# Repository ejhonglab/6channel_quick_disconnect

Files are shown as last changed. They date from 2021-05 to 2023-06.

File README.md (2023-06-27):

This assembly aims to allow rapidly exchanging groups of 6 odor vials.

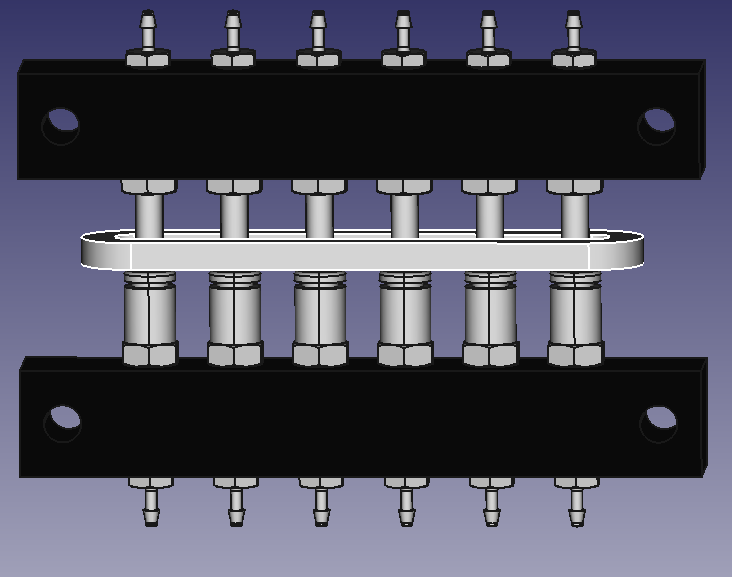
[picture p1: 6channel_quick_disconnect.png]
CAD model


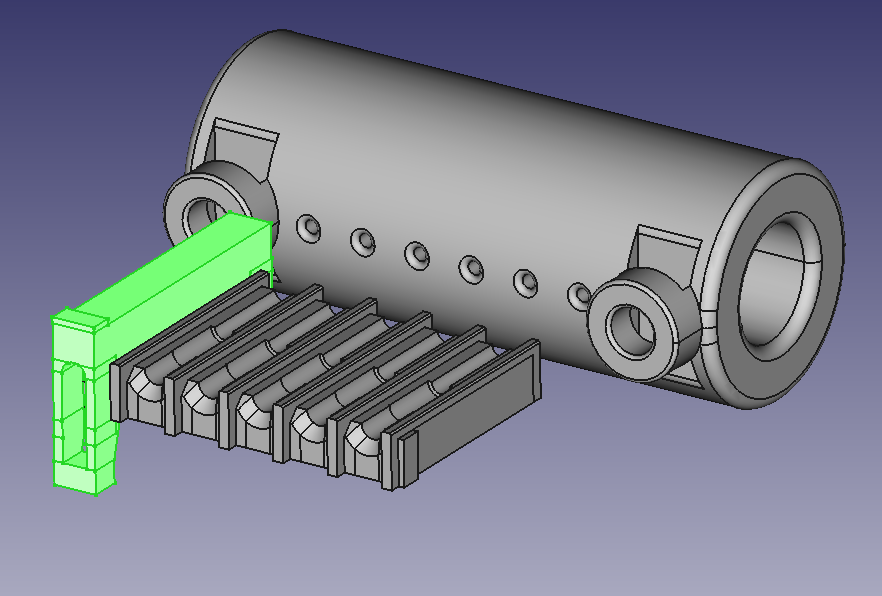
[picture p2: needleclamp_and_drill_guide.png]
Needleclamp and drill guide


### Bill of materials

| Description | McMaster Part Number | Quantity |
| ---         | ---                  | ---      |
| 5/32" OD tube stem to 10-32 thread | [5779K623](https://www.mcmaster.com/5779K623) | 6 |
| Junction block (6 position, 10-32 thread) | [5091K61](https://www.mcmaster.com/5091K61) | 1 + 1 per-exchangeable-side |
| Female 5/32" OD push-to-connect to 10-32 thread | [7880T115](https://www.mcmaster.com/7880T115) | 6 per-exchangeable-side |
| 10-32 thread to barb for 1/16" ID tube | [2974K123](https://www.mcmaster.com/2974K123) | 6 + 6 per-exchangeable-side (2 packs of 10) | 
| Release bar | N/A (3D printed from `release_bar.stl`) | 1 |
| Mounting screws | [92185A992](https://www.mcmaster.com/92185A992) | 1 (25 pack) |

The [tube stems (5779K623)](https://www.mcmaster.com/5779K623) can each be replaced with
a combination of an additional [female push-to-connect (7880T115)](https://www.mcmaster.com/7880T115)
and a [female-to-female tube stem adapter (5779K349)](https://www.mcmaster.com/5779K349)
, which is substantially cheaper at current prices. Making this substitution will
introduce another joint that could be more likely to leak.

See our [11-channel olfactometer repo](https://github.com/ejhonglab/11channel_olfactometer)
for the context in which we use this assembly, along with a parts list to build it.

### Assembly

To drill the 6 holes the needles will be inserted into (in the 1/4" ID, 3/8" OD PTFE
tube; see 11 channel olfactometer bill of materials), print
`needle_drill_guide_for_ptfe_tube.stl` and lightly clamp it do the PTFE tube using M3
fasteners. `needle_drill_guide_for_ptfe_tube.3mf` should contain the same model as the
STL, but also has a support enforcer to only generate supports in a place where they
should be easy to remove. Use a smaller drill than the diameter of the needles (maybe <=
3/64"), and you should be able to get several uses out of the drill guide. If making
several rows of holes, offset them enough so that the needles will not interfere with
each other when inserted.

`needleclamp_top_with_supports.stl` should be printed in an orientation where one side
of each latch is flat against the bed, so that layer lines do not make the latch more
fragile.  I used PETG and a 0.4mm nozzle, without many changes to the bridging settings,
and no supports added. Any internal supports would make the part harder to clean up, and
doing so would risk damaging the latches, so the part has a rectangle opposite the space
for the needle, which you should cut off of each latch (e.g. with a razor blade). An
initial attempt to print the part using a 0.6mm nozzle did not make good parts, because
the bridging performance was different, although limited internal supports or different
settings could possibly fix that. I leave one of these parts semi-permanently attached
to the end of each odor vial I'm actively using, to minimize setup time.

### 3D-printed parts

All parts (except the drill guide) should be printed with high infill. I used 100%.

I printed most parts on a Prusa i3 MK3S with PETG filament. All parts should be
printable with either a 0.4 or 0.6mm nozzle, *except* `needleclamp_top.stl`, which I so
far only got good parts with a 0.4mm nozzle.

I used PrusaSlicer
`2.2`-`2.3` to slice the `.stl` files to `.gcode`.

#### Regenerating STLs

To generate `release_bar.stl`:
1. Open `6channel_quick_disconnect.FCStd` in FreeCAD
2. Select `release_bar` in the tree view at the left. May need to expand
   `6channel_quick_disconnect` first.
3. `File->Export` (or `Ctrl-e`). Under the `Files of type:` menu at the bottom, select
   `STL Mesh (*.stl *.ast)`. Rename file to `release_bar.stl`. Press `Save`.

`needle_clamp_and_drill_guide.FCStd` contains the models for:
- `needleclamp_top_with_supports.stl`
- `needleclamp_bottom.stl`
- `needle_drill_guide_for_ptfe_tube.stl`

The `*.FCStd` files were produced with FreeCAD `0.19`-`0.20`.

The models for the McMaster-Carr parts in `6channel_quick_disconnect.FCStd` came from
the McMaster website.

### Operation

#### Push-to-connect (air inputs to odor vials)

Before matching the two sides of this assembly (i.e. pushing the tube stems into the
female push-to-connect adapters), check that you have a release bar placed around the
row of male tube stems. Then, firmly squeeze both sides of the assembly from the
aluminum passthru blocks. To disconnect the two sides of the assembly, press the release
bar down (so it presses all of the release rings on the female push-to-connect
fittings), and then pull the two sides apart.

#### Needleclamp (odor vial outputs)

Both the top and bottom of the needleclamp have a ridge to indicate which side has a
wider internal diameter. The clamp tops should be inserted so that their ridge is on the
same side as the ridge on the clamp bottom, and the section of the needle covered with
the PTFE tubing should go in this half of the clamp.

The section of the needle with PTFE tube over it should go (at most) halfway down the
needleclamp top, as if the PTFE overlaps with the thinner internal diameter of the
needleclamp top, the top and bottom of the clamp won't close all the way. When all slots
in the clamp are populated, the top surfaces of all the clamp tops should be flat. If
any are sticking out, check whether the PTFE section is inserted too far. If the needles
are not in a straight enough line to insert, it also likely indicates a clamp is not
seated fully.

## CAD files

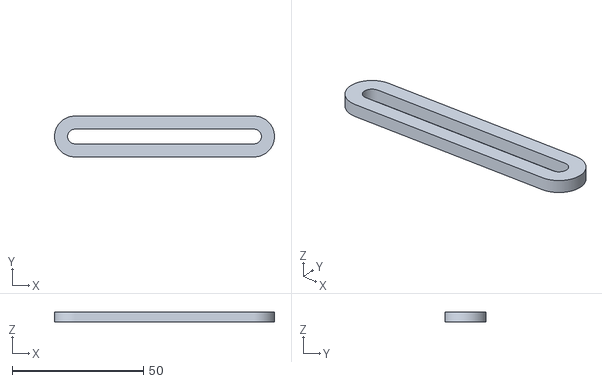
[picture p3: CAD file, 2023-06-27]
release_bar.stl
83.9 x 15.6 x 4.00

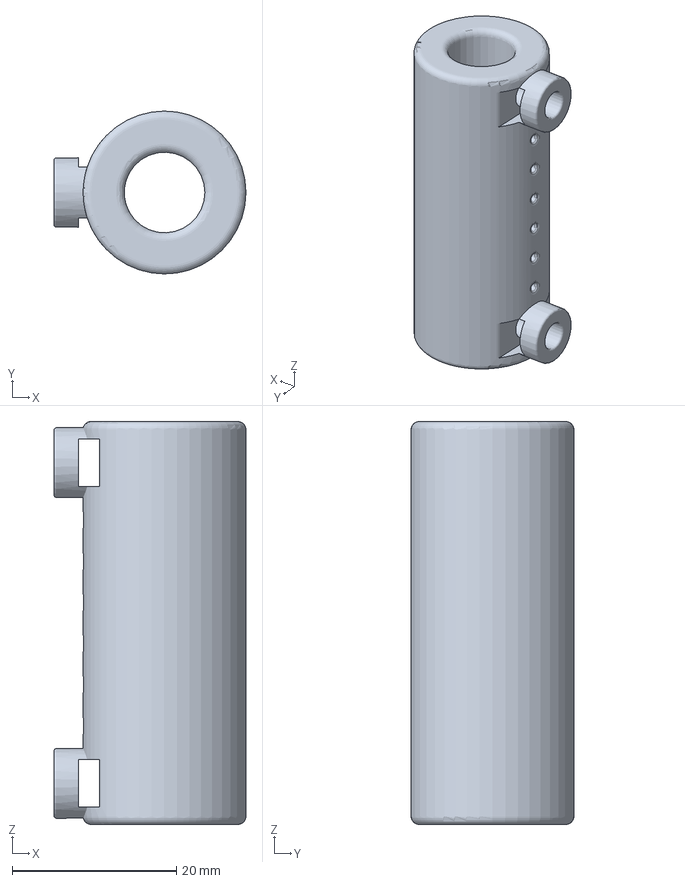
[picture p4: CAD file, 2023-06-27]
needle_drill_guide_for_ptfe_tube.3mf
23.3 x 19.8 x 49.0 mm

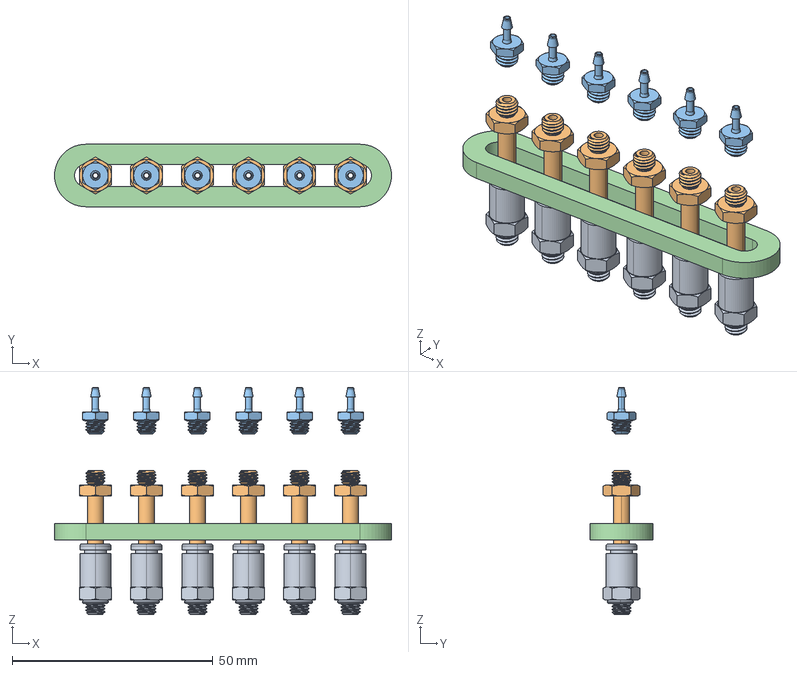
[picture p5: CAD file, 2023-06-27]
6channel_quick_disconnect.FCStd
83.9 x 15.6 x 56.5 mm
p2c_f_array
p2c_m_array
top_barb_array_mirrored
release_bar

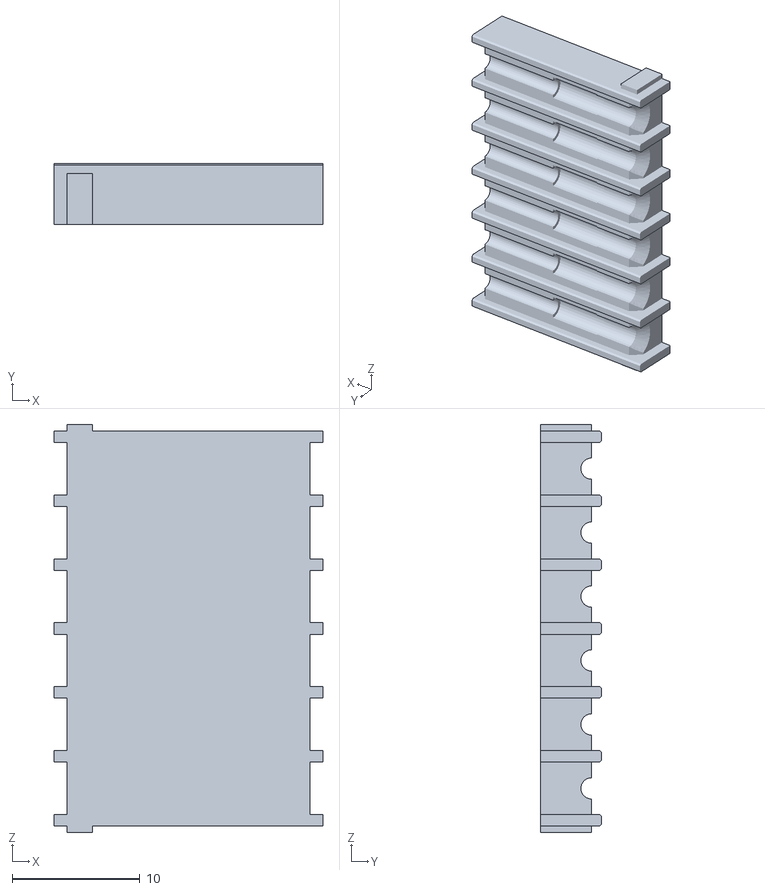
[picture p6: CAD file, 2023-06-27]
needleclamp_bottom.stl
21.0 x 4.80 x 31.9

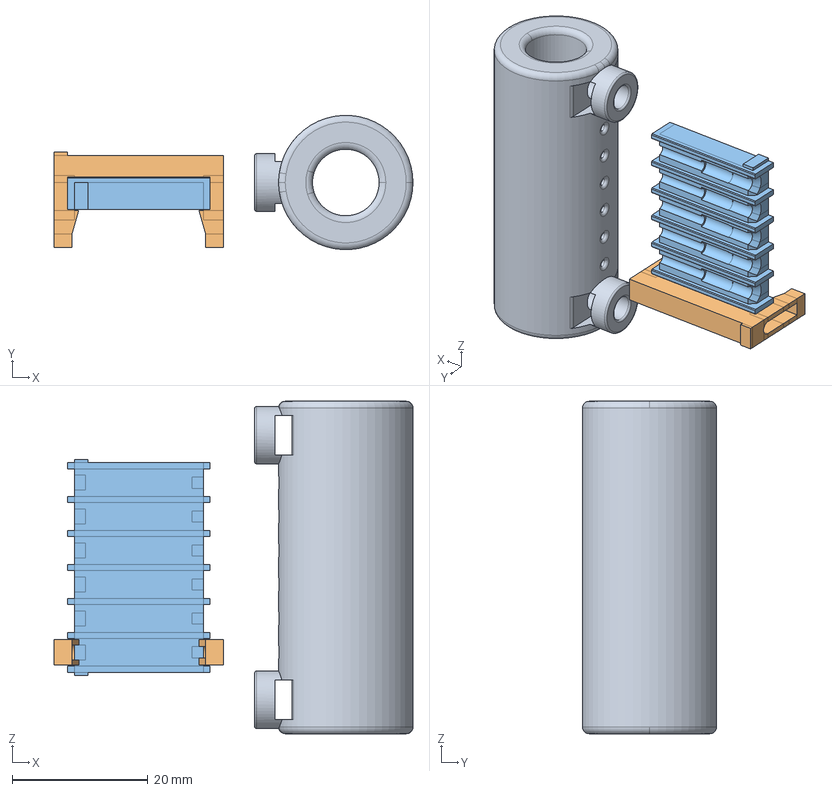
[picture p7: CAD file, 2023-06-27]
needle_clamp_and_drill_guide.FCStd
52.9 x 19.8 x 49.0 mm
needle_drill_guide_for_ptfe_tube
needleclamp_top_with_supports
needleclamp_bottom

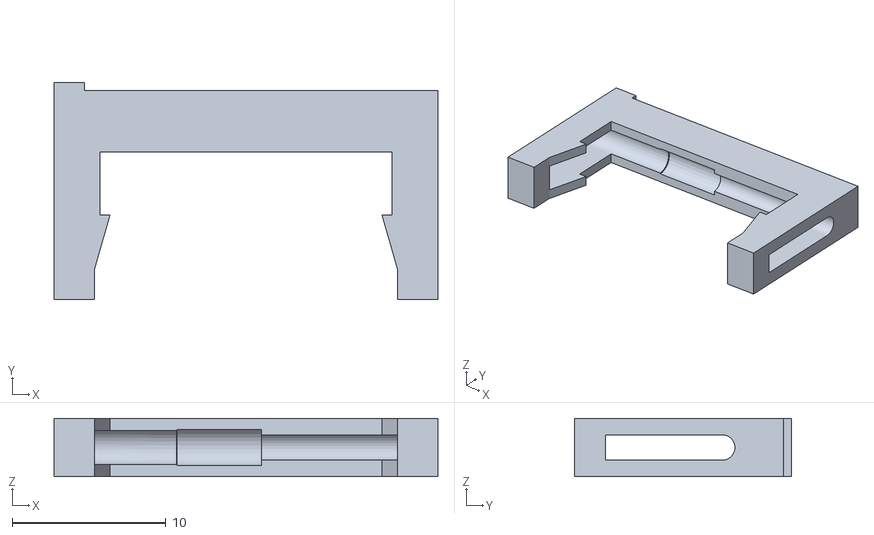
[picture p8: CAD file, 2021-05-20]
needleclamp_top_with_supports.stl
25.0 x 14.1 x 3.80

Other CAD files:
needle_drill_guide_for_ptfe_tube.stl

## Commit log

2020-12-07 Initial commit. Have untested prototype release bar STL / gcode
    [6channel_quick_disconnect.FCStd, release_bar.stl]
2020-12-07 Add black color to junction blocks. First attempt at github markdown BOM table
    [6channel_quick_disconnect.FCStd]
2020-12-07 Decreased release bar height 8mm->4mm to account for wrong CAD of male connectors. Made it wider + sliced w/ 100% infill.
    [6channel_quick_disconnect.FCStd, release_bar.stl]
2021-02-05 Add mounting screws to BOM.
2021-04-23 Move parts of this assembly into a Part container. Necessary for current use in 11channel_olfactometer FCStd file.
    [6channel_quick_disconnect.FCStd]
2021-05-01 Add initial prototype of needle drill guide
    [needle_drill_guide_for_ptfe_tube.FCStd, needle_drill_guide_for_ptfe_tube.stl]
2021-05-06 Add initial prototype STLs for needleclamp. Almost working but may need to add tolerances / widen so it can be sliced in other orientation without being too fragile, because supports are hard to remo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
    [needle_drill_guide_for_ptfe_tube.FCStd, needle_drill_guide_for_ptfe_tube.stl, rough_needleclamp_bottom.stl, rough_needleclamp_top.stl]
2021-05-20 Lengthen needleclamp + add parametric supports to require no special care besides orientation when slicing clamp tops. Add tactile ridge to indicate direction on each needleclamp part.
    [6channel_quick_disconnect.FCStd, needle_drill_guide_for_ptfe_tube.FCStd, rough_needleclamp_bottom.stl, rough_needleclamp_top.stl]
2021-05-21 Add .3mf and .gcode files for needleclamp parts (2x bottoms and 12x tops).
    [needleclamp_2x_bottom_12x_top.3mf]
2023-06-27 Add assembly / operation instructions and link to 11channel_olfactometer repo, check models are current working versions, remove GCode now that nozzle is no longer 0.4mm, update BOM (+ alternative pa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
    [6channel_quick_disconnect.FCStd, needle_clamp_and_drill_guide.FCStd, needle_drill_guide_for_ptfe_tube.3mf, needle_drill_guide_for_ptfe_tube.FCStd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]
